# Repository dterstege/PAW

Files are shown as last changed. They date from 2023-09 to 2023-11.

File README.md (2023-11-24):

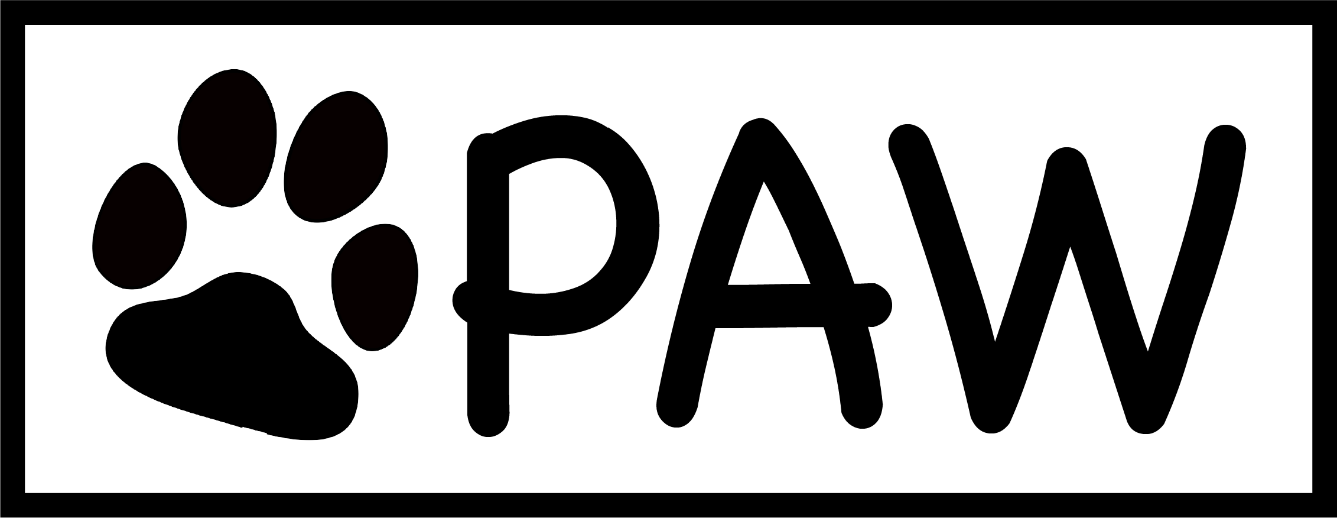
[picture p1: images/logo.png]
# PAW   

### OVERVIEW ###
**PAW** is a 3D **P**rintable **A**rduino-based **W**heel logger.  An inexpensive (~$75 CAD) alternative to commercial running wheel systems, PAW provides 1/100 second resolution while tracking the wheel running activity of mice in the home cage.  This compact and wireless design is easy to assemble, with the electronics themselves taking under an hour to put together.  The ease of manufacturing is matched by the ease of analysis, as PAW saves all running wheel data to an on-board MicroSD card in an easily accessible CSV format.

For detailed instructions on the assembly and use of the PAW system, please see the appropriate sections of this GitHub repository.

Current Versions:
- Dome: [v1](https://github.com/dterstege/PAW/tree/main/BUILD/DOME/v1) (10/2023)
- Base: [v1](https://github.com/dterstege/PAW/tree/main/BUILD/BASE/v1) (10/2023)
- PAW: [v2](https://github.com/dterstege/PAW/tree/main/PAW/v2) (11/2023)

If you find this running wheel useful and use it in your experiments, please [cite the original PAW manuscript](#cite).



---

### TABLE OF CONTENTS ###

| Section  | Description | 
| ------------- | ------------- | 
| [1. ASSEMBLY](#assembly)   | How to assemble the PAW components  |
| [2. USER GUIDE](#guide)   | How to use the PAW to monitor wheel running  |
| [3. FAQ](#faq) | Frequently asked questions |
| [4. CITATION](#cite) | How to cite PAW |
| [5. CONTACT US](#contact)  | Where to reach us with questions  |

---

<a name="assembly"/>

### 1. ASSEMBLY ###

- #### 1.1 Files #####
  
| File Name | File Type | Link |
| ---------- | --------- | -------- |
| Dome | F3D (Fusion360), STL | [v1](https://github.com/dterstege/PAW/tree/main/BUILD/DOME/v1) |
| Base | F3D (Fusion360), STL | [v1](https://github.com/dterstege/PAW/tree/main/BUILD/BASE/v1) |
| PAW | Arduino IDE | [v2](https://github.com/dterstege/PAW/tree/main/PAW/v2) |
  
- #### 1.2 Parts ####

parts

| Designator | Component | Quantity | Source |
| ---------- | --------- | -------- | ------ |
| Mouse Igloo | Bio-Serv Mouse Igloo (K3570) | 1 | [Bio-Serv](https://www.bio-serv.com/product/Mouse_Igloo.html) |
| Fast-Trac Wheel | Bio-Serv Fast-Trac (K3251) | 1 | [Bio-Serv](https://www.bio-serv.com/product/Mouse_Igloo.html) |
| Arduino Microcontroller | Arduino UNO R3 | 1 | [3D Printing Canada](https://3dprintingcanada.com/products/arduino-uno-r3-with-usb-cable?variant=14108869001259&ab_version=A&gclid=Cj0KCQjw4NujBhC5ARIsAF4Iv6c0mkKVTBclo_TsJNL7h-8sDUEFHimAureF2F8ooSkBpy2Fl_JDz5waAlbCEALw_wcB) |
| Hall Sensor | Hall Effect Magnetic Sensor (KY-003) | 1 | [Amazon](https://www.amazon.ca/HiLetgo-Effect-Magnetic-Sensor-Arduino/dp/B01NBE2XIR/ref=sr_1_11?hvadid=667691407406&hvdev=c&hvlocphy=9001320&hvnetw=g&hvqmt=e&hvrand=10586946240617008813&hvtargid=kwd-300772771853&hydadcr=24939_13701817&keywords=a3144+hall+effect+sensor&qid=1695678062&sr=8-11) |
| Real-Time Clock (RTC) | Real Time Clock Module (DS321) | 1 | [Amazon](https://www.amazon.ca/Geekstory-Precision-AT24C32-Arduino-Raspberry/dp/B085XT4RJF?th=1) |
| MicroSD Reader | MicroSD Card Reader Module | 1 | [Amazon](https://www.amazon.ca/Willwin-Adapter-Reader-Module-Arduino/dp/B077P18N78/ref=sr_1_11?crid=3KO1Q53MW70PJ&keywords=microsd%2Bmodule&qid=1695677807&s=electronics&sprefix=microsd%2Bmodule%2Celectronics%2C132&sr=1-11&th=1) |
| Boost Converter | T64 DC to DC Step Up Voltage Module | 1 | [Amazon](https://www.amazon.ca/10Pcs-DC-DC-Boost-Converter-Modules/dp/B07MTH1R39/ref=sr_1_16?crid=DW2K8JW3GU05&keywords=5v+dc+dc+step+up&qid=1688484902&sprefix=5v+dc+dc+step+up%2Caps%2C116&sr=8-16) |
| Battery Holder | 3 AA Battery Holder | 1 | [Amazon](https://www.amazon.ca/LampVPath-Battery-Holder-Leads-Wires/dp/B07WRQ3XTJ/ref=sr_1_5?crid=2LUS3M99AU56B&keywords=3+aa+battery+holder&qid=1695678384&sprefix=3+AA%2Caps%2C177&sr=8-5) |
| AA Batteries | High-Capacity Rechargable AA Batteries | 3 | [Amazon](https://www.amazon.ca/EBL-Capacity-Rechargeable-Batteries-Included/dp/B01DZYSK72/ref=sr_1_34?crid=3G5IRWDPO9SK7&keywords=aa%2Bbatteries&qid=1695678735&sprefix=AA%2Caps%2C203&sr=8-34&th=1) |
| CR2032 Battery | Lithium CR2023 Battery | 1 | [Amazon](https://www.amazon.ca/Energizer-2032BP-6-Lithium-Battery-Count/dp/B0002RID4G/ref=sr_1_5?crid=2178CZ8F2PMRY&keywords=cr2032&qid=1695678625&sprefix=CR%2Caps%2C185&sr=8-5&th=1) |
| MicroSD Card | 32 GB High Speed MicroSD Card | 1 | [Amazon](https://www.amazon.ca/Silicon-Power-Speed-MicroSD-Adapter/dp/B07RRX7XWF/ref=sr_1_6?crid=MLFCRD98PNQZ&keywords=sp%2B3d%2Bnano&qid=1695680447&sprefix=sp%2B3d%2Bnano%2Caps%2C141&sr=8-6&th=1) |
| Silicone Wire | 22 AWG Silicone Wire | 70 cm | [Amazon](https://www.amazon.ca/CBAZYTM-Stranded-Gauge-colors-Electrical/dp/B075M7YZXC/ref=sr_1_2_sspa?crid=6MECIRCG3J2E&keywords=hook%2Bup%2Bwire%2B22%2Bawg&qid=1695679152&sprefix=hook%2Bup%2Bwire%2B22%2Caps%2C123&sr=8-2-spons&sp_csd=d2lkZ2V0TmFtZT1zcF9hdGY&th=1) |
| Magnet | Magnet | 1 | [Amazon](https://www.amazon.ca/Craft-Magnets-Ceramic-Refrigerator-Whiteboard/dp/B07S75MD7X/ref=sr_1_10?crid=16ACULN3BZIQI&keywords=magnet&qid=1695680080&sprefix=magnet%2Caps%2C176&sr=8-10&th=1) |
| 3D Printing Filament | 1.75 mm PLA Filament | 98 g | [Amazon](https://www.amazon.ca/AMZ3D-1-75mm-Printer-Filament-Black/dp/B01BZ5ND8O/ref=asc_df_B01BZ5ND8O/?tag=googleshopc0c-20&linkCode=df0&hvadid=292982668511&hvpos=&hvnetw=g&hvrand=1112761188398538947&hvpone=&hvptwo=&hvqmt=&hvdev=c&hvdvcmdl=&hvlocint=&hvlocphy=9001318&hvtargid=pla-380498731113&th=1) |
| M3x8 Screw | M3x8 Screw | 3 | [Amazon](https://www.amazon.ca/Fullerkreg-Socket-Stainless-Machine-Quantity/dp/B07CJ9BRCK/ref=sr_1_26?crid=36BMALKGCKR0I&keywords=m3x8&qid=1695681161&s=hi&sprefix=m3x8%2Ctools%2C124&sr=1-26&th=1) |
| M3x12 Screw | M3x12 Screw | 4 | [Amazon](https://www.amazon.ca/dp/B07CK58Z48/ref=twister_B07MNPL15J?_encoding=UTF8&th=1) |

- 
  - Solder and flux applied as needed during assembly
  - Electrical tape can be used as needed to cover any on-board LEDs
  - Heat shrink tubing to cover junctions in silicone wires
  - Non-toxic hot glue to fix magnet to the underside of the Fast-Trac wheel
 
- #### 1.3 3D Printing ####
  - Download [Dome](https://github.com/dterstege/PAW/tree/main/BUILD/DOME) and [Base](https://github.com/dterstege/PAW/tree/main/BUILD/BASE) STL files
  - Slice g-code in your slicer of choice (e.g., [Ultimaker Cura](https://ultimaker.com/software/ultimaker-cura/))
  - Print Settings (Based on Creality Ender 3 V2 3D Printer):
    - Nozzle: 0.4 mm
    - Layer Height: 0.12 mm
    - Perimeter Wall Thickness: 1.2 mm
    - Infill: 50%
    - Minimum Support Overhang Angle: 59
  - Estimated Time: ~ 2 days
  - prints
- #### 1.4 Electronics ####
  - De-solder pins from:
    -  Hall Effect Sensor
        - NOTE: most of these sensors have on-board LEDs which can be removed during this process and soldered over
    -  RTC
    -  MicroSD Reader Module
  - Cut 15 x 7 cm lengths of wire (ideally, in 6 different colours as follows):
    - 3 x Power Wire (red)
    - 4 x Ground Wire (black)
    - 3 x Signal A (green)
    - 2 x Signal B (yellow)
    - 2 x Signal C (blue)
    - 1 x Signal D (white)
  - Strip 7 - 8 mm from each end of each length of wire to allow for solid connections in Arduino headers
  - Junctions: in this manual, junctions refer to soldering multiple wires together to split a connection (e.g., joining 2 ground wires together so that two components can be plugged into the same ground header on the Arduino)
    - Ground Junctions (x2):
      - ground_junction
      - Step 1: Cut one ground wire down to 3 cm, strip 1 cm from this end
      - Step 2: Strip the silicone coating from the 2 cm - 2.5 cm marks of a second ground wire
      - Step 3: Wrap the 1 cm exposed end of the shorter ground wire around the exposed section of the longer ground wire. Solder this connection and then protect with heat shrink tubing.
      - Step 4: Final junction should allow for two components to be plugged into the same Arduino header
    - Power Junction (x1):
      - power_junction
      - Step 1: Strip the silicone coating from 3 cm - 3.5 cm marks on one power wire to expose a junction point
      - Step 2: Strip the silicone coating from 3 cm - 3.5 cm marks on a second power wire to expose a junction point
      - Step 3: Wrap these two wires around each other at these junction points. Solder this connetion and then protect with heat shrink tubing.
      - Step 4: Final junction should allow for 3 components to be powered from the same 5V Arduino header.
  - Wiring (Fritzing as guide):
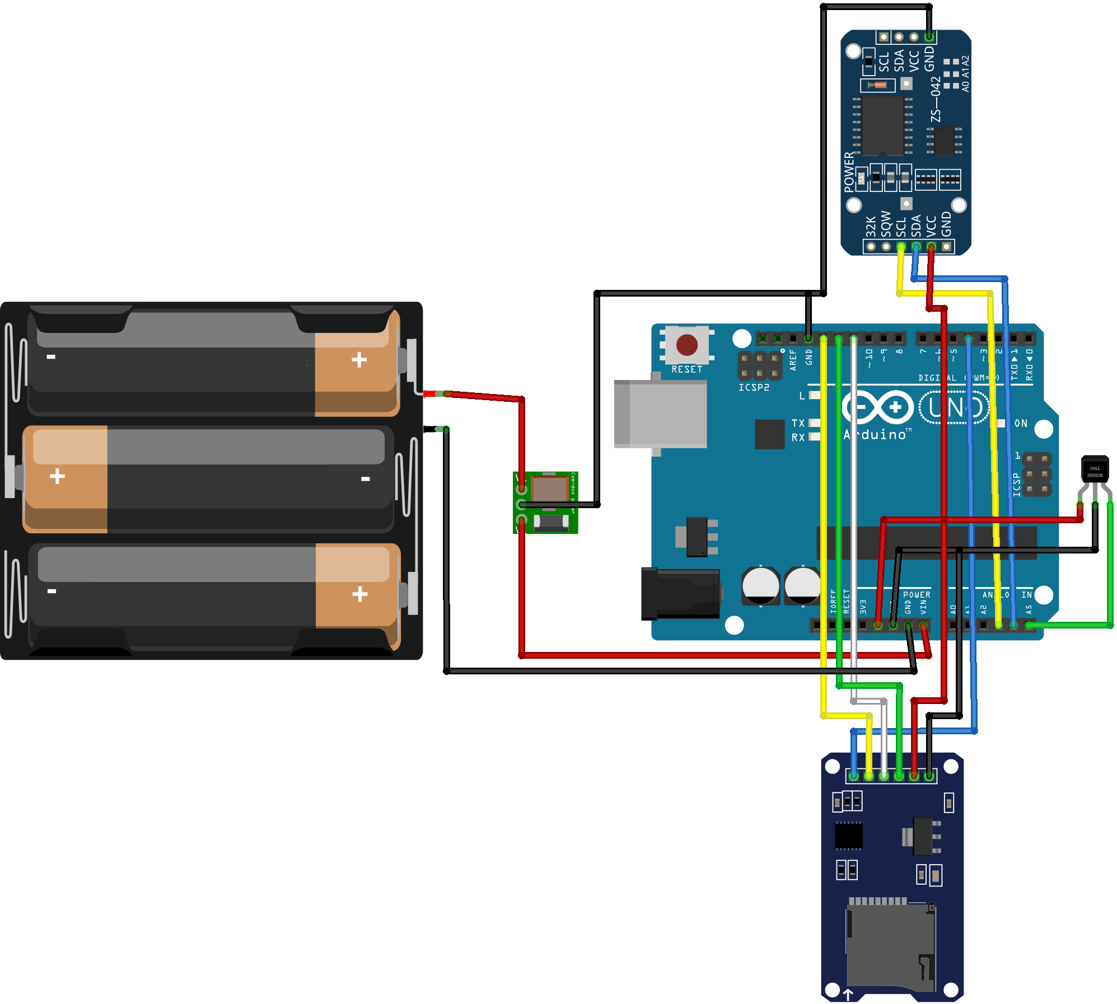
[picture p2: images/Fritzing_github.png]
fritzing
    - 
    - Boost Converter:
      - VO: to header Vin on Arduino
      - GND: to GND on Arduino
      - Vin: Power from batteries
    - Batteries:
      - Power to Boost Converter
      - Ground to Arduino
    - Hall Effect Sensor:
      - pin 1: GND to GND
      - pin 2: to 5V
      - pin 3: to header A5
    - RTC:
      - GND: to GND
      - VCC: to 5V
      - SDA: to header A4
      - SCL: to header A3
    - MicroSD Card Module:
      - CS: to header 4 (digital)
      - SCK: to header 13 (digital)
      - MOSI: to header 11 (digital)
      - MISO: to header 12 (digital)
      - VCC: to 5V
    - NOTE: Trim wires as needed for the most compact orientation possible
  - Solder wires in place, using flux as needed
  - elec

- #### 1.5 Putting it all together ####
  - Insert CR2032 Battery in RTC module
  - Insert MicroSD Card in MicroSD Reader module
  - Insert 3 x AA Batteries in the Battery Holder
  - Insert four M3x12 Screws through the underside of the Base in the holes in the center ring
  - basescrew
  - Turn the base component over and fit these screws through the holes of the Arduino (this will keep it in place) and arrange the battery holder on top of the electronics
  - basearduino
  - Place the Dome overtop, with the Hall Effect Sensor lined-up with the hole in the Dome
  - On the underside of the Base,secure the Dome to the Base with three M3x8 Screws along the perimeter of the Base
  - screw
  - The Bio-Serv Mouse Igloo will now fit securely over this whole assembly
  - igloo
  - To interact with the Hall Effect Sensor, a magnet needs to be glued to the inside of the Fast-Trac Wheel
  - magnet
  - Now the wheel can be attached to the igloo - completing the assembly
  - assembled

---

<a name="guide"/>

### 2. USER GUIDE ###
- #### 2.1 Programming the Arduino Microcontroller ### 
  - Download the latest [Arduino IDE](https://www.arduino.cc/en/software)
  - Open this application and, using the *Manage Libraries...* function in the *Tools* tab, install the following libraries:
    - RTClib (This will allow us to control the DS3231 RTC)
    - SD (This will allow us to interface into the MicrSD Card)
  - Open the [PAW Arduino Code](https://github.com/dterstege/PAW/tree/main/PAW) in the IDE
  - Set the date and time for the RTC by adjusting the following lines:
  - 
         rtc.setTime(17, 30,00);
         rtc.setDate(31, 10, 2023);
  - The first of these lines sets the time of day in a 24 hour, hh, mm, ss format (in the above example, the time of day is 5:30 PM)
  - The second line sets the date in a dd, mm, yyyy format (in the above example, the date is October 31, 2023)
  - Code can now be flashed to the PAW system
 - #### 2.2 Accessing and Analyzing Data ####
   - PAW data can be accessed directly through the output CSV files on the MicroSD Card.
   - A new file will be generated on each day (*added in PAW, v2*)
   - Each line in this file will contain a timestamp denoting at which point each wheel rotation occurred, at 1/100th of a second resolution. 

---

<a name="faq"/>

### 3. FAQ ###
**Frequently Asked Questions**

We will update this section as questions come up.

---

<a name="cite"/>

### 4. CITATION ###

This section will be update should the manuscript outlining PAW be accepted for publication.

---

<a name="contact"/>

### 5. CONTACT US ###
- Dylan Terstege (Developed PAW) 
  - twitter-icon_16x16[@dterstege](https://twitter.com/dterstege) 
  - Mail
<dylan.terstege@ucalgary.ca>

- Jonathan Epp (Principal Investigator) 
  - https://epplab.com

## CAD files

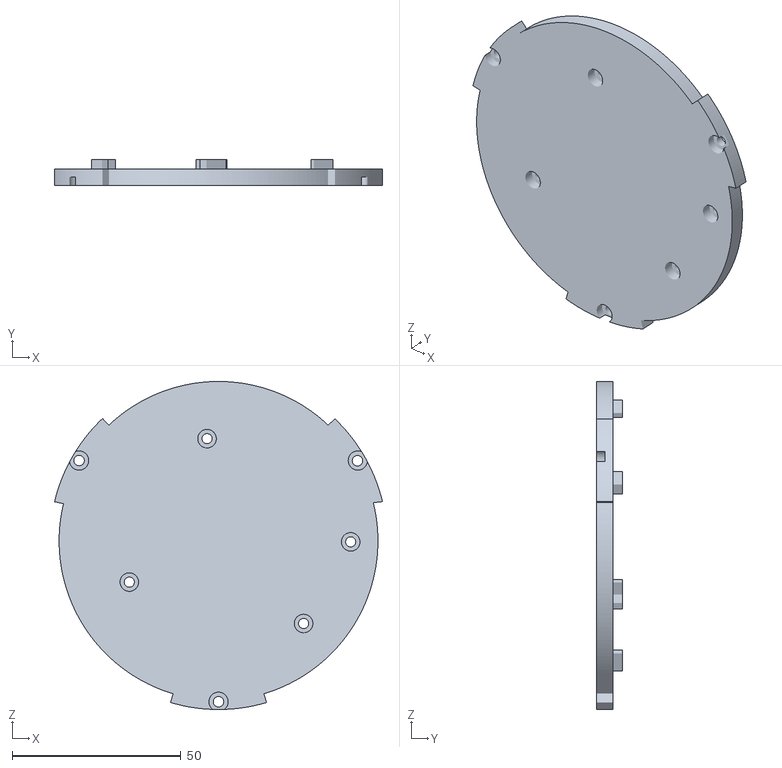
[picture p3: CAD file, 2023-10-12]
BUILD/BASE/v1/Base_v1.stl
97.1 x 7.60 x 97.1

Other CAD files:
BUILD/BASE/v1/Base_v1.f3d
BUILD/DOME/v1/Dome_v1.f3d

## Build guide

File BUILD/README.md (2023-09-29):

### BUILD ###
This section contains the build files for PAW.

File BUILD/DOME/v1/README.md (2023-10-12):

PAW - Dome, v1

Initially uploaded October 12, 2023

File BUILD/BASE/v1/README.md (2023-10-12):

PAW - Base, v1

Initially uploaded October 12, 2023
